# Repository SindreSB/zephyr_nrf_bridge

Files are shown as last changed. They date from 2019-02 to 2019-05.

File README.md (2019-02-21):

# Zephyr based bridge for Dexcom G4

Highly WIP, and not at all working

## Installation
This repo contains a west manifest file, which enables this to be a manifest repo when using the west tool.

Steps to get up and running:
1. Follow install guide for zephyr/west
1. Clone this repo 
1. Set the variables:
    * ZEPHYR_BASE=\<path to zephyr>
    * ZEPHYR_TOOLCHAIN_VARIANT=gnuarmemb
    * GNUARMEMB_TOOLCHAIN_PATH=\<path to gnu>
1. cd into the app directory
1. Use west build with the propper arguments and -s .
    * west build -b nrf52_pca10040 -s .

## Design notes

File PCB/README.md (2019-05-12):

# nBridge PCB

The nBridge consists of a LiPo charger, a 3.3 regulator, a BL652 BLE module and a CC2500 module

## Versions
V1: Base design. Used very small parts which are too difficult to reliably solder
V2: Lower part count with larger components, as well as micro-USB instead of USB-C type connector.

## Parts list
The partslist is still changing, and it is easier to export it from the most recent desgin files than to have possibly outdatet information here. All passives are 0804 size componetns, while hte regulator and LDO are SOT23. The LEDs are 0603. 

## PCB 
The PCB can be found on https://aisler.net/p/FUKRPVUI. Newer, and maybe untested, revisions might be available there as well. The full source of the PCB is in the folder nBridge, though some symbols might be in different libraries not included. Currently, only revision 1 has been ordered.

## Pinout (V1)
### NRF52 - CC2500
| BL652 pin(V1) | nRF52832 pin | Function | 
|----|-|-----|
| 31 | P0.19 | CC2500 - MOSI | 
| 32 | P0.31 | CC2500 - CLK |
| 33 | P0.30 | CC2500 - MISO |
| 35 | P0.28 | CC2500 - GDO0 |
| 36 | P0.27 | CC2500 - GDO2 |
| 37 | P0.26 | CC2500 - CSn |
| 34 | P0.29/AIN5 | Analog input of battery voltage |
| 38 | P0.25 | Enable battery voltage measurement |
| 20 | P0.05 | LED0 |
| 19 | P0.06 | LED1 |
| 5  | SWDIO | SWDIO |
| 6  | SWDCLK | SWDCLK |
| 7  | P0.21 | nRST |
| 9  | P0.18 | SWO |

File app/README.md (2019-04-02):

To run on NRF52-DK
1) set ZEPHYR_TOOLCHAIN_VARIANT=gnuarmemb
1) set GNUARMEMB_TOOLCHAIN_PATH=C:\gnu_arm_embedded
1) west build -b nrf52_pca10040
1) west flash

On nrf52840-dongle (requires nrfutil in path):
1) set ZEPHYR_TOOLCHAIN_VARIANT=gnuarmemb
1) set GNUARMEMB_TOOLCHAIN_PATH=C:\gnu_arm_embedded
1) west build -b nrf52840_pca10059
1) nrfutil pkg generate --hw-version 52 --sd-req=0x00 --application build/zephyr/zephyr.hex --application-version 1 pkg.zip
1) nrfutil dfu usb-serial -pkg pkg.zip -p COM6

On custom boards (out-of-tree):
1) set ZEPHYR_TOOLCHAIN_VARIANT=gnuarmemb
1) set GNUARMEMB_TOOLCHAIN_PATH=C:\gnu_arm_embedded
1) west build -b \<board\> -- -DBOARD_ROOT="."
1) west flash

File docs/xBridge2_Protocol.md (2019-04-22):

# xBridge2 Protocol spesification
The xBridge2 protocol is used by LBridge as well as others? to transmit BG measurements to the xDrip+ application. Any transmitter using this protocol can use the Bluetooth Wixel collector? in xDrip+. 

## Service and characteristics
The xBridge2 protocol consists of a single service, with one characteristic. These coincide with the HM10 bluetooth module used in the original Wixel bridge. 

xBridge2 service 

UUID: 0000ffe0-0000-1000-8000-00805f9b34fb

Communications characteristic: 

UUID: 0000ffe1-0000-1000-8000-00805f9b34fb

Permissions: Read, Write, Notify

## Packets
The following packet types are part of the xBridge2 protocol:

### Measurement record
The measurement record is sent for every new measurement received, as well as when sendingn historic measurements.

Name|Type|Size [bytes]|Value|Description
--- | --- | --- | --- | --- 
Size|Uint8|1 [0]|0x15|Size of the packet - should be 21
Packet type|Uint8|1 [1]|0x00|Code identifying data packet. Always 00 for a Dexcom data packet
Raw|Uint32|4 [2:5]||Raw ISIG value
Filtered|Uint32|4 [6:9]||Filtered ISIG value
Transmitter battery|Uint8|1 [10]||Transmitter battery value, as received from transmitter
Bridge battery|Uint8|1 [11]||Battery percentage 0-100 as an integer
Transmitter id|Uint32|4 [12:15]||Transmitter id of the Dexcom transmitter
Delay|Uint32|4 [16:19]||Offset since measurement in milliseconds?, only positive values makes sense here.
Protocol level|Uint8|1 [20]|0x01|Byte representing xBridge functionality, xBridge2 = 0x01

NOTE: Protocol level is ignored by xDrip and since a standard BLE package is 20bytes, it may be omitted to avoid having to split transmission in multiple packets. Note that size still have to be 0x15 for the packet to be correctly identified. A size 0x11 represents a xBridge1 packet(?), without support for historic data.

Due to C alignment, a C struct with the above types will have the wrong size and byte positions. Such a struct must be "packed" for the decoding in xDrip+ to work.

This packet should be used for both for current and historic measurements. For historic measurements, the raw, filtered and delay are the only fields that change, the Transmitter battery, Bridge battery and Transmitter id should always contain up to date information. 

### Measurement acknowledgement
The acknowledgement package is sent after a measurement is received. 

Name|Type|Size|Value|Description
--- | --- | --- | --- | --- 
Size|Uint8|1 [0]|0x02|Number of bytes in the packet - will always be 2
Packet type|Uint8|1 [1]|0xF0|Packet type- should be 0xF0

Historically the Wixel went to sleep upon reception, or after a 3 sec timeout, but the xDrip app can support receiving another measurement after an acknowledgement has been sent. 

## TxId packet
This packet is sent fomr the app to the device to set the transmitter id to filter on.

Name|Type|Size [bytes]|Value|Description
--- | --- | --- | --- | --- 
Size|Uint8|1 [0]|0x06|Number of bytes in package
Packet type|Uint8|1 [1]|0x01|Packet type- txid is 0x01
Transmitter Id|Uint32|4 [2:5]||Dexcom transmitter id, int encoded

##  Beacon package
The beacon package is sent from the device to the app

Name|Type|Size [bytes]|Value|Description
--- | --- | --- | --- | --- 
Size|Uint8|1 [0]|0x07|Number of bytes in packet 
Packet type|Uint8|1 [1] |0xF1|Packet type - beacon type is 0xF1
TxId|Uint32|4 [2:5]||Dexcom transmitter id, int encoded
Protocol level|Uint8|1 [6]|0x01|xBridge protocol level

NOTE: In the original xBridge2 documentation, there is a typo which states the size of the beacon package is 0x06, though xDrip correctly uses the size 0x07 to identify a beacon package.

## Conversion from transmitter id to int representation:
Define the table [0-9A-Y], which contains 32 characters. To index into this table, 5 bits are needed. To convert to, from string, each letter is replaced by its index in the table. The resulting ID is 25 bits long, and is stored in a Uint32, all other bits being 0. 

## Sending historic data to xDrip - special note
The protocol itself does not impose any restirctions on when a value is sent, but the xDrip+ app discards values older than the last value received. This means that if you are using the historic measurements functionality, you MUST send the oldest value first. The sender thus have to buffer measurements, and upon connection, transmit the oldest value first. xDrip also ignore measurements within two minutes of another measurement, as well as measurements from before the last calibration. No error will be indicated to the sender in any of these events.

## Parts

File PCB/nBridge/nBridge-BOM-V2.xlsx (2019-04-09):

Reference | Quantity | Value | Footprint | Digikey part number |  | Datasheet
C2 C4 C1 C3 | 4 | 1uF | Capacitor_SMD:C_0402_1005Metric | 1276-1067-1-ND |  | ~
D1 | 1 | LED | LED_SMD:LED_0603_1608Metric | 160-1447-1-ND |  | ~
D2 | 1 | LED | LED_SMD:LED_0603_1608Metric | 160-1446-1-ND
J1 | 1 | USB_C_Receptacle_USB2.0 | SharedFootprints:12401610E4#2A | 12401610E4#2ACT-ND |  | https://www.usb.org/sites/default/files/documents/usb_type-c.zip
J2 | 1 | Conn_01x06 | SharedFootprints:Conn_Pas_01x06_1.27mm | Do not buy |  | ~
J3 | 1 | Conn_01x02 | Connector_PinHeader_2.54mm:PinHeader_1x02_P2.54mm_Vertical | Do not buy |  | ~
R1 R7 | 2 | 10k | Resistor_SMD:R_0402_1005Metric | 1276-3530-1-ND |  | ~
R2 | 1 | 1k35 | Resistor_SMD:R_0402_1005Metric | P560AWDKR-ND | 560 instead of 1k35 gives 240mA IFAST | ~
R3 | 1 | 6k | Resistor_SMD:R_0402_1005Metric | P5.6KAWCT-ND | 5.6k instead of 6k | ~
R4 R5 | 2 | 220R | Resistor_SMD:R_0402_1005Metric | 541-4247-1-ND |  | ~
R6 | 1 | 27k | Resistor_SMD:R_0402_1005Metric | P27KAWCT-ND |  | ~
SW1 | 1 | Switch-SPDT | SharedFootprints:CSS-121XB | 563-1091-1-ND |  | ~
U1 | 1 | TPS7A0533PYKAR | SharedFootprints:TPS7A0533PYKAR | 296-52115-1-ND
U2 | 1 | BQ25100YFPR | SharedFootprints:BQ25100YFPR | 296-39931-1-ND
U3 | 1 | BL652 | RF_Module:Laird_BL652 | BL652-SA-01-CT-ND |  | http://cdn.lairdtech.com/home/brandworld/files/Datasheet%20-%20BL652.pdf
U4 | 1 | CC2500Module | nBridge:CC2500Module | Do not buy

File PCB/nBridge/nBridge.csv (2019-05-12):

Reference | Quantity | Value | Footprint | Datasheet | Category | DK_Datasheet_Link | DK_Detail_Page | Description | Digi-Key_PN | Family | MPN | Manufacturer | Status
C3 C1 C2 C4 | 4 | 1uF | Capacitor_SMD:C_0805_2012Metric | ~
D1 | 1 | GREEN LED | LED_SMD:LED_0603_1608Metric | ~
D2 | 1 | RED LED | LED_SMD:LED_0603_1608Metric | ~
J1 | 1 | 473460001 | digikey-footprints:USB_Micro_B_Female_0473460001 | https://www.molex.com/pdm_docs/sd/473460001_sd.pdf | Connectors, Interconnects | https://www.molex.com/pdm_docs/sd/473460001_sd.pdf | /product-detail/en/molex/0473460001/WM17141CT-ND/1782474 | CONN RCPT USB2.0 MICRO B SMD R/A | WM17141CT-ND | USB, DVI, HDMI Connectors | 473460001 | Molex | Active
J2 | 1 | Conn_01x06 | SharedFootprints:Conn_Pas_01x06_1.27mm | ~
J3 | 1 | Conn_01x02 | Connector_PinHeader_2.54mm:PinHeader_1x02_P2.54mm_Vertical | ~
R1 | 1 | R | Resistor_SMD:R_0805_2012Metric | ~
R4 R5 | 2 | 220R | Resistor_SMD:R_0805_2012Metric | ~
R6 | 1 | 27k | Resistor_SMD:R_0805_2012Metric | ~
R7 | 1 | 10k | Resistor_SMD:R_0805_2012Metric | ~
SW1 | 1 | Switch-SPDT | SharedFootprints:CSS-121XB | ~
U1 | 1 | LP5907MFX-3_3_NOPB | digikey-footprints:SOT-753 | http://www.ti.com/general/docs/suppproductinfo.tsp?distId=10 | Integrated Circuits (ICs) | http://www.ti.com/general/docs/suppproductinfo.tsp?distId=10 | /product-detail/en/texas-instruments/LP5907MFX-3.3-NOPB/296-38557-1-ND/5034443 | IC REG LINEAR 3.3V 250MA SOT23-5 | 296-38557-1-ND | PMIC - Voltage Regulators - Linear | LP5907MFX-3.3/NOPB | Texas Instruments | Active
U2 | 1 | MCP73812T-420I_OT | digikey-footprints:SOT-753 | http://www.microchip.com/mymicrochip/filehandler.aspx?ddocname=en528273 | Integrated Circuits (ICs) | http://www.microchip.com/mymicrochip/filehandler.aspx?ddocname=en528273 | /product-detail/en/microchip-technology/MCP73812T-420I-OT/MCP73812T-420I-OTCT-ND/1979800 | IC LI-ION/LI-POLY CTRLR SOT23-5 | MCP73812T-420I/OTCT-ND | PMIC - Battery Chargers | MCP73812T-420I/OT | Microchip Technology | Active
U3 | 1 | BL652 | RF_Module:Laird_BL652 | http://cdn.lairdtech.com/home/brandworld/files/Datasheet%20-%20BL652.pdf |  |  |  |  |  |  | BL652-SA-01 | LAIRD
U4 | 1 | CC2500Module | nBridge:CC2500Module

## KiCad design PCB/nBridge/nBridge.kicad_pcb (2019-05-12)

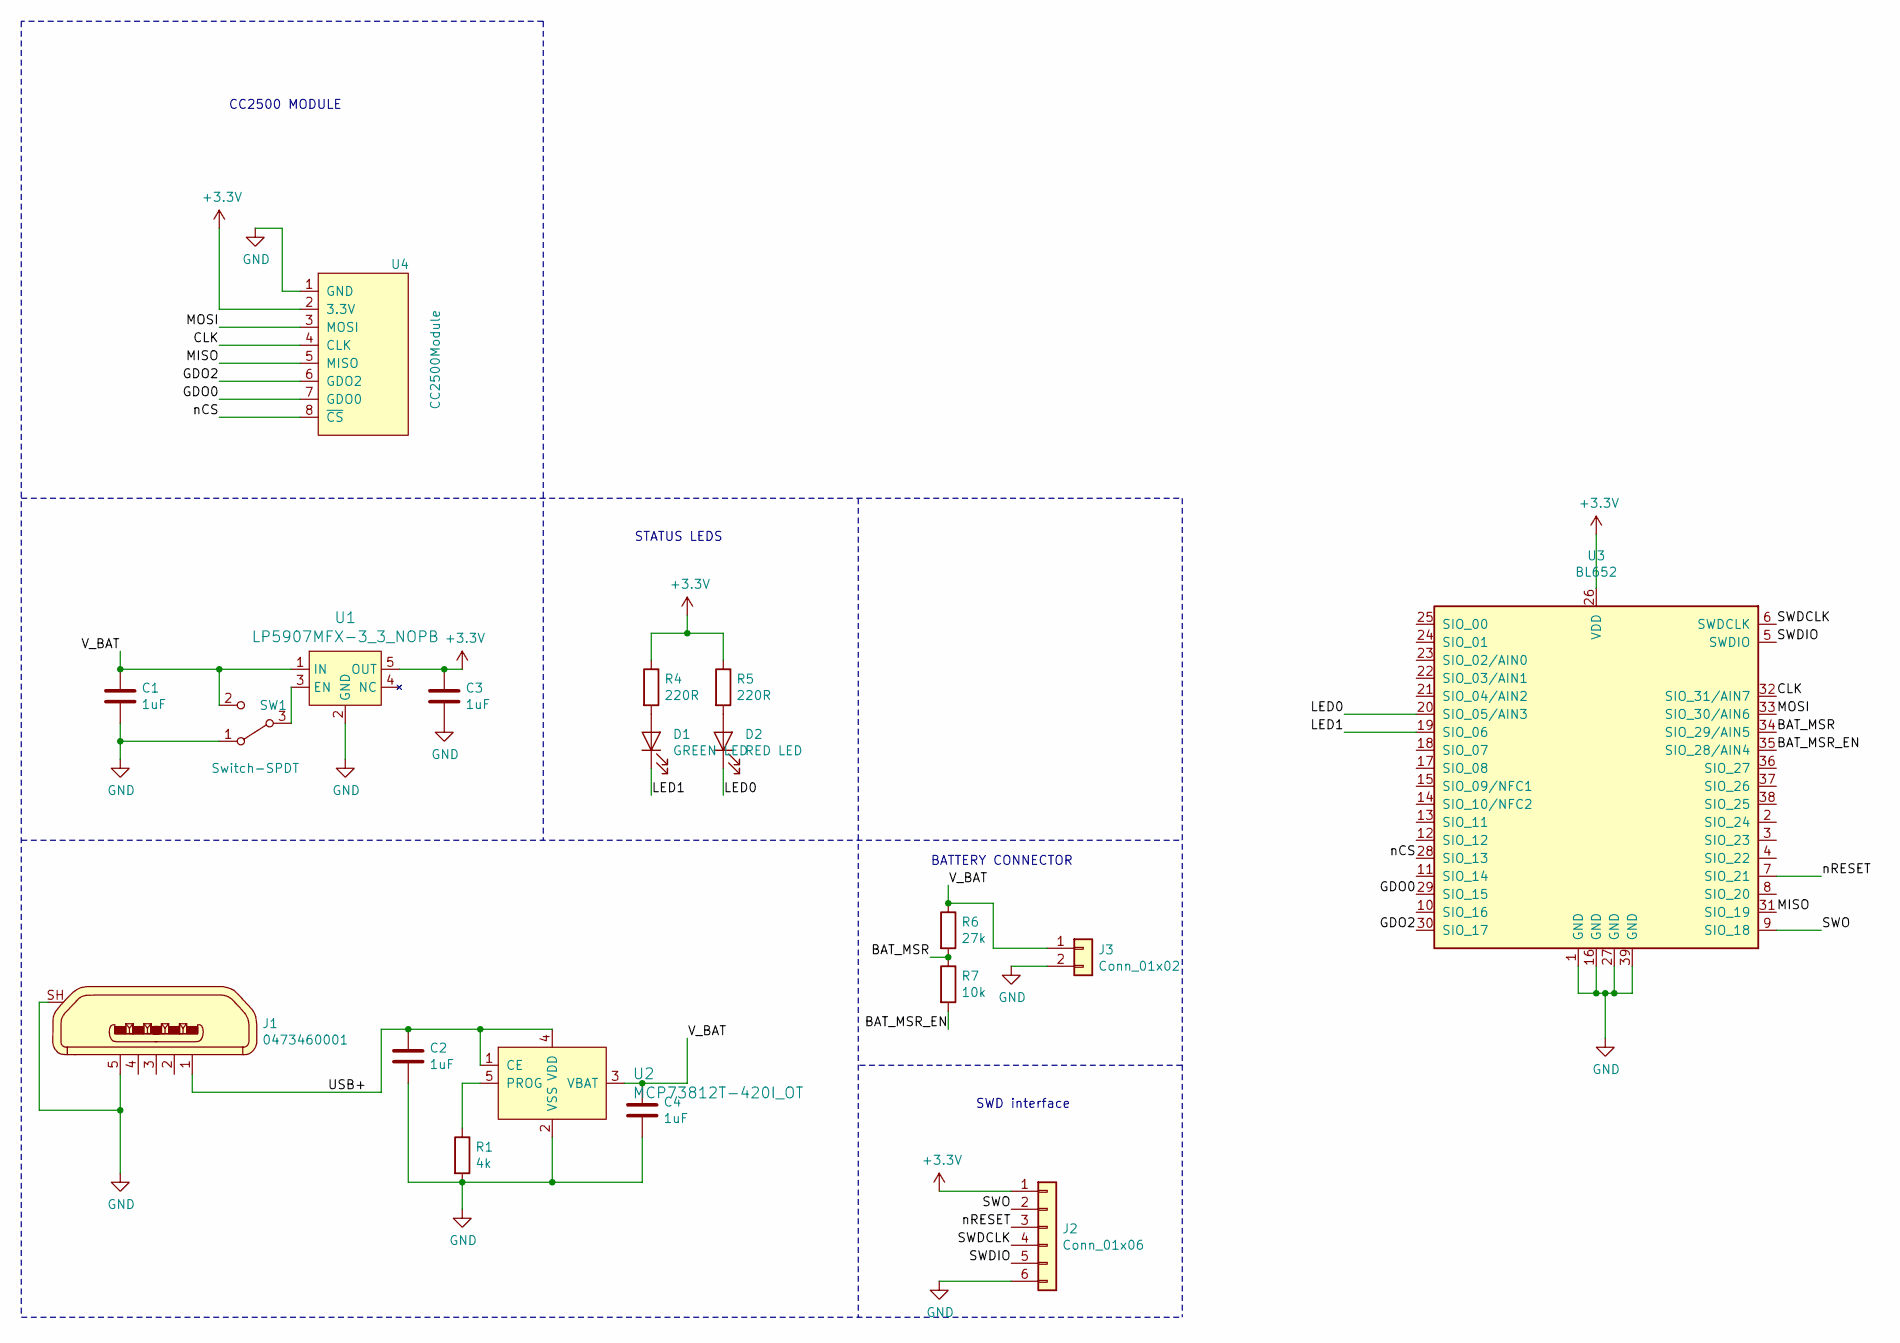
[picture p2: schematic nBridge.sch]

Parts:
C1, C2, C3, C4: 1uF; C_0805_2012Metric
D1: GREEN LED; LED_0603_1608Metric
D2: RED LED; LED_0603_1608Metric
J1: 0473460001; USB_Micro_B_Female_0473460001; MPN 0473460001; Digi-Key_PN WM17141CT-ND
J2: Conn_01x06; Conn_Pas_01x06_1.27mm
J3: Conn_01x02; PinHeader_1x02_P2.54mm_Vertical
R1: 4k; R_0805_2012Metric
R4, R5: 220R; R_0805_2012Metric
R6: 27k; R_0805_2012Metric
R7: 10k; R_0805_2012Metric
SW1: Switch-SPDT; CSS-121XB
U1: LP5907MFX-3_3_NOPB; SOT-753; MPN LP5907MFX-3.3/NOPB; Digi-Key_PN 296-38557-1-ND
U2: MCP73812T-420I_OT; SOT-753; MPN MCP73812T-420I/OT; Digi-Key_PN MCP73812T-420I/OTCT-ND
U3: BL652; Laird_BL652
U4: CC2500Module

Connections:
+3V3: C3.1, J2.1, R4.1, R5.1, U1.5 (OUT), U3.26 (VDD), U4.2 (3.3V)
/BAT_MSR: R6.2, R7.1, U3.34 (SIO_29/AIN5)
/BAT_MSR_EN: R7.2, U3.35 (SIO_28/AIN4)
/CLK: U3.32 (SIO_31/AIN7), U4.4 (CLK)
/GDO0: U3.29 (SIO_15), U4.7 (GDO0)
/GDO2: U3.30 (SIO_17), U4.6 (GDO2)
/LED0: D2.1 (K), U3.20 (SIO_05/AIN3)
/LED1: D1.1 (K), U3.19 (SIO_06)
/MISO: U3.31 (SIO_19), U4.5 (MISO)
/MOSI: U3.33 (SIO_30/AIN6), U4.3 (MOSI)
/SWDCLK: J2.4, U3.6 (SWDCLK)
/SWDIO: J2.5, U3.5 (SWDIO)
/SWO: J2.2, U3.9 (SIO_18)
/USB+: C2.1, J1.1, U2.1 (CE), U2.4 (VDD)
/V_BAT: C1.1, C4.1, J3.1, R6.1, SW1.2 (C), U1.1 (IN), U2.3 (VBAT)
/nCS: U3.28 (SIO_13), U4.8 (~CS)
/nRESET: J2.3, U3.7 (SIO_21)
GND: C1.2, C2.2, C3.2, C4.2, J1.5, J1.SH, J2.6, J3.2, R1.2, SW1.1 (A), U1.2 (GND), U2.2 (VSS), U3.1 (GND), U3.16 (GND), U3.27 (GND), U3.39 (GND), U4.1 (GND)
unnamed: D1.2 (A), R4.2
unnamed: D2.2 (A), R5.2
unnamed: R1.1, U2.5 (PROG)
unnamed: SW1.3 (B), U1.3 (EN)

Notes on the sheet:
SWD interface
BATTERY CONNECTOR
STATUS LEDS
CC2500 MODULE

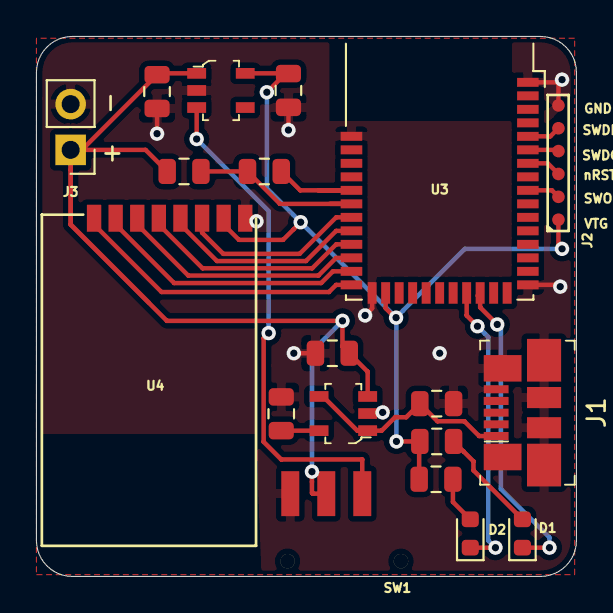
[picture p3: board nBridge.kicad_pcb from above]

Board: 2 copper layers, 30.0 x 30.0 mm, 19 parts (0 on the bottom side), 22 nets.

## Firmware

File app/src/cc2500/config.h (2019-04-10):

/**
 * @file config.h
 * @author your name (you@domain.com)
 * @brief Contains for hardware used to connect to CC2500
 * @version 0.1
 * @date 2019-04-10
 * 
 * @copyright Copyright (c) 2019
 * 
 */
#include <autoconf.h>

#define GPIO_OUT_DRV_NAME CONFIG_CC2500_GPIO

// Correct pins must be configured in DTS
#define SPI_DRV_NAME CONFIG_CC2500_SPI

#define SPI_CS_PIN CONFIG_CC2500_CS_PIN
#define GDO0_PIN CONFIG_CC2500_GDO0_PIN
#define GDO2_PIN CONFIG_CC2500_GDO2_PIN

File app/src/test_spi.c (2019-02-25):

#include <zephyr.h>
#include <logging/log.h>
#include <logging/log_ctrl.h>

//#include <autoconf.h>

#include <device.h>
#include <gpio.h>
#include <spi.h>

#include "cc2500/cc2500_spi.h"
#include "cc2500/cc2500_reg.h"
#include "cc2500/cc2500.h"

#include "cc2500/utils.h"

// Does this work for NRF52 -yes, but not general enough?
#define GPIO_OUT_DRV_NAME "GPIO_0"
#define GPIO_OUT_PIN  17

#define SPI_DRV_NAME SPI_2_LABEL
#define SPI_CS_PIN 12
// #define SPI_2_LABEL					    DT_NORDIC_NRF_SPI_40023000_LABEL
// #define SPI_2_MISO_PIN					DT_NORDIC_NRF_SPI_40023000_MISO_PIN
// #define SPI_2_MOSI_PIN					DT_NORDIC_NRF_SPI_40023000_MOSI_PIN
// #define SPI_2_SCK_PIN					DT_NORDIC_NRF_SPI_40023000_SCK_PIN

#define SEC_TO_TICK(sec) sec * 1200 // Trial and error, not accurate

LOG_MODULE_REGISTER(test_cc2500);

u8_t data_buffer[64];

// This will have to be replaced by a macro
// Replace cc_ with a given prefix
static gpio_callback_t cc_gdo0_cb;
static gpio_callback_t cc_gdo2_cb;
cc2500_ctx_t cc_ctx = {
    .gdo0_cb = &cc_gdo0_cb,
    .gdo2_cb = &cc_gdo2_cb,
};

static struct k_work work;

volatile bool handeled_package = true;

void read_package_from_cc(struct k_work *item)
{
    handeled_package = true;
    LOG_INF("GDO0 asserted, which indicates end of packet received");

    // Config should have put the device into idle mode at end of package
    // but just to be sure
    cc2500_mode_idle(&cc_ctx);
    
    u8_t rxbytes, status;
    cc2500_read_status_reg(&cc_ctx, CC2500_REG_RXBYTES, &rxbytes, &status);

    LOG_INF("Status is: %02X, rxbytes is: %02X", status, rxbytes);

    // If overflow, ignore it all and retry
    if ((rxbytes & 0x80)) { 
        LOG_INF("Overflow in RX FIFO, ignore data");
        
    }
    else if ((rxbytes & 0x7F) > 0 && (status & 0x07) > 0) {
        LOG_INF("RXBYTES is: %02X", rxbytes);   
        u8_t num_bytes_rx = rxbytes & 0x7F; // Mask bit 7, which is overflow
        LOG_INF("%d bytes received", num_bytes_rx);
        
        cc2500_read_burst(&cc_ctx, CC2500_REG_RXFIFO, data_buffer, num_bytes_rx, NULL);

        printk("Data received: ");
        int i;
        for(i = 0; i < num_bytes_rx; i++) {
            printk("%02X ", data_buffer[i]);
        }


        uint16_t raw, filtered; 
        raw = data_buffer[12] << 8 | data_buffer[12];
        filtered = data_buffer[14] << 8 | data_buffer[15];
        float rawMmol = isigToMmol(convertFloat(reverse16(raw)));
        float filteredMmol = isigToMmol(convertFloat(reverse16(filtered)));


        printk("\n");
        printk("Raw: %f\n", rawMmol);
        printk("Fil: %f\n", filteredMmol);

    }    

    LOG_INF("Flushing RX FIFO");
    cc2500_flush_rxfifo(&cc_ctx);

    LOG_INF("Going back into RX mode");
    cc2500_mode_receive(&cc_ctx, 0);
    
    LOG_INF("Handler completed, listening...");
    return;
}


void submit_package_read(struct device *gpiob, struct gpio_callback *cb,
		    u32_t pins)
{
    if (!handeled_package) return;

    LOG_INF("Submitting read package job");
    k_work_init(&work, read_package_from_cc);
    k_work_submit(&work);
}


void test_cc2500(void) 
{
    LOG_INF("Testing CC2500");
    u8_t value, status;

    LOG_INF("Resetting CC2500");
    cc2500_send_strobe(&cc_ctx, CC2500_CMD_SRES, &status);

    LOG_INF("Asserting XTAL is stable");
    if(!cc2500_verify_osc_stabilization(&cc_ctx)) {
        LOG_INF("CC2500 didn't become ready in time");
        return;
    }
    
    LOG_INF("Reading off values to ensure CC2500 is working");
    cc2500_read_status_reg(&cc_ctx, CC2500_REG_PARTNUM, &value, &status);
    LOG_INF("Partnum: 0x%02X, should be 0x80", value);

    cc2500_read_status_reg(&cc_ctx, CC2500_REG_VERSION, &value, &status);
    LOG_INF("Version: 0x%02X, should be 0x03", value);

    // Write required register values
    LOG_INF("Writing Dexcom config to device");
    cc2500_write_register(&cc_ctx, CC2500_REG_PATABLE,      0x00, NULL);
    cc2500_write_register(&cc_ctx, CC2500_REG_IOCFG0,	    0x01, NULL);
    cc2500_write_register(&cc_ctx, CC2500_REG_PKTLEN,	    0xFF, NULL);
    cc2500_write_register(&cc_ctx, CC2500_REG_PKTCTRL1,	    0x04, NULL);
    cc2500_write_register(&cc_ctx, CC2500_REG_PKTCTRL0,	    0x05, NULL);
    cc2500_write_register(&cc_ctx, CC2500_REG_ADDR,	        0x00, NULL);
    cc2500_write_register(&cc_ctx, CC2500_REG_CHANNR,	    0x00, NULL);

    cc2500_write_register(&cc_ctx, CC2500_REG_FSCTRL1,	    0x0F, NULL);
    cc2500_write_register(&cc_ctx, CC2500_REG_FSCTRL0,	    0x00, NULL);
    
    cc2500_write_register(&cc_ctx, CC2500_REG_FREQ2,	    0x5D, NULL);
    cc2500_write_register(&cc_ctx, CC2500_REG_FREQ1,	    0x44, NULL);
    cc2500_write_register(&cc_ctx, CC2500_REG_FREQ0,	    0xEB, NULL);
    
    cc2500_write_register(&cc_ctx, CC2500_REG_FREND1,	    0xB6, NULL);
    cc2500_write_register(&cc_ctx, CC2500_REG_FREND0,	    0x10, NULL);
    
    cc2500_write_register(&cc_ctx, CC2500_REG_MDMCFG4,	    0x7A, NULL);
    cc2500_write_register(&cc_ctx, CC2500_REG_MDMCFG3,	    0xF8, NULL);
    cc2500_write_register(&cc_ctx, CC2500_REG_MDMCFG2,	    0x73, NULL);
    cc2500_write_register(&cc_ctx, CC2500_REG_MDMCFG1,	    0x23, NULL);
    cc2500_write_register(&cc_ctx, CC2500_REG_MDMCFG0,	    0x3B, NULL);
    
    cc2500_write_register(&cc_ctx, CC2500_REG_DEVIATN,	    0x40, NULL);
    
    cc2500_write_register(&cc_ctx, CC2500_REG_MCSM2,	    0x07, NULL);
    cc2500_write_register(&cc_ctx, CC2500_REG_MCSM1, 	    0x30, NULL);
    cc2500_write_register(&cc_ctx, CC2500_REG_MCSM0,	    0x18, NULL);
    
    cc2500_write_register(&cc_ctx, CC2500_REG_FOCCFG,	    0x16, NULL);
    
    cc2500_write_register(&cc_ctx, CC2500_REG_FSCAL3,	    0xA9, NULL);
    cc2500_write_register(&cc_ctx, CC2500_REG_FSCAL2,	    0x0A, NULL);
    cc2500_write_register(&cc_ctx, CC2500_REG_FSCAL1,	    0x00, NULL);
    cc2500_write_register(&cc_ctx, CC2500_REG_FSCAL0,	    0x11, NULL);
    
    cc2500_write_register(&cc_ctx, CC2500_REG_AGCCTRL2,	    0x03, NULL);
    cc2500_write_register(&cc_ctx, CC2500_REG_AGCCTRL1,	    0x00, NULL);
    cc2500_write_register(&cc_ctx, CC2500_REG_AGCCTRL0,	    0x91, NULL);
    
    cc2500_write_register(&cc_ctx, CC2500_REG_TEST2,	    0x81, NULL);
    cc2500_write_register(&cc_ctx, CC2500_REG_TEST1,	    0x35, NULL);
    cc2500_write_register(&cc_ctx, CC2500_REG_TEST0,	    0x0B, NULL);
    
    cc2500_write_register(&cc_ctx, CC2500_REG_FOCCFG,	    0x0A, NULL);
    
    cc2500_write_register(&cc_ctx, CC2500_REG_BSCFG,	    0x6C, NULL);

    LOG_INF("Registering callback for GDO0");
    cc2500_register_gdo0_handler(&cc_ctx, submit_package_read, GPIO_INT_EDGE | GPIO_INT_ACTIVE_HIGH);

    LOG_INF("Going into RX mode");
    cc2500_mode_receive(&cc_ctx, 0);

    LOG_INF("All setup completed, listening...");
}

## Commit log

2019-01-23 Add initial samples
2019-01-30 Remove attempt to sample MISO
    Instead simply reading the status byte and checking that first bit is 0 after device has been sleeping or off should be sufficient
2019-02-22 Replace printk with LOG_INF except for packet reception
2019-04-01 Add board definitions for both breakout and nBridge
2019-04-01 FIx board definition for n_bridge board
2019-04-02 Update readme and remove out of tree board from CMakeList
2019-04-09 Start tracking PCB
    [nBridge-BOM-V2.xlsx, nBridge-BOM..xlsx, nBridge.csv, nBridge.kicad_pcb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]
2019-04-09 Update pinout to correspond to PCB
2019-04-10 Add DT overlay for nrf52840-mdk board
2019-04-10 Make pin configurations into kconfig options
2019-04-23 Remove RTC
    [nBridge.sch]
2019-05-01 Simplify design, fewer and more easily solderable components
    [nBridge.kicad_pcb, nBridge.sch]
2019-05-01 Minor modifications
    [nBridge.kicad_pcb]
2019-05-02 Update part values and remove unused silkscreen
    [nBridge.csv, nBridge.kicad_pcb, nBridge.sch]
2019-05-03 Add 3d models to V2
    [nBridge.kicad_pcb]
2019-05-03 Add USB model
    [nBridge.kicad_pcb]
2019-05-03 Update PCB readme
